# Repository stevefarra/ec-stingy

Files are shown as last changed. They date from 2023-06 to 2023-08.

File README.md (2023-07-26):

<p align="center">
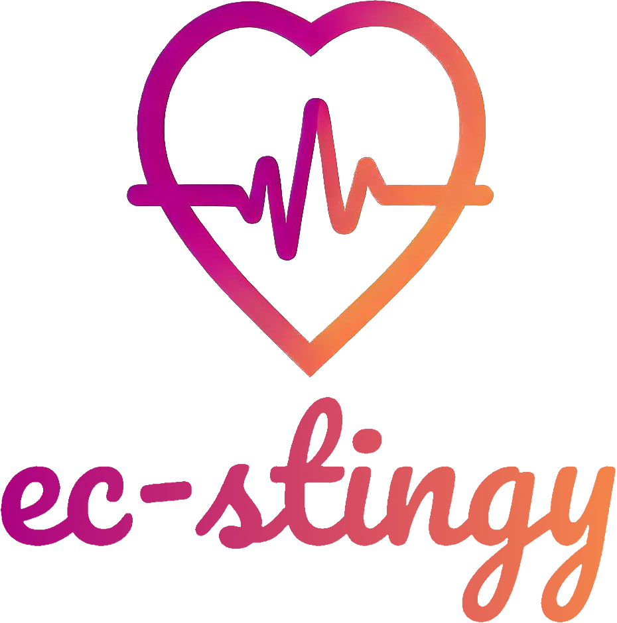
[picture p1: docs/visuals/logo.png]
Project logo
  
</p>

# ec-stingy
The EC(stin)G(y) provides an end-to-end design and implementation of a cost-effective, compact electrocardiogram. It connects to a computer via USB, monitoring a patient's cardiac signal and heart rate over time.

This project can serve as a template for any device measuring the heart's electrical activity and can be easily adapted to the user's needs. By open-sourcing the design files and code, the project aims to make medical hardware and technology more accessible and reduce the barrier to entry for prototyping.

## Directory Overview
Each folder corresponds to a specific stage of development or a component of the final product.

[`algorithm/`](algorithm/) - A simulation suite for prototyping digital signal filtering and peak detection.

[`firmware/`](firmware/) - Contains the program loaded into the MCU on-board the PCB.

[`spice/`](spice/) - Another simulation suite for prototyping the ECG analog front-end circuitry.

[`pcb/`](pcb/) - Schematic, footprint, and manufacturing files for the printed circuit board.

[`gui/`](gui/) - A desktop program to view the cardiac signal and heart rate readings over time.

[`docs/`](docs/) - Datasheets, README graphics, cited research papers, and other miscellanea.

## License

ec-stingy is licensed under the [MIT License](LICENSE). Unless otherwise stated, the repository owner authors all content, including source code, schematics, documentation, plots, animations, etc.

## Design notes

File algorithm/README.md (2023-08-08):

# Algorithm prototyping
## Directory overview
[`algorithm.m`](algorithm/algorithm.m) - An Octave script for design, implementation, and visualization of the signal conditioning, R-peak detection, and heart rate calculation program used by this project.

[`algorithm.c`](algorithm/algorithm.c) - A real-time C adaptation of the program contained in the Octave script, optimized for minimal time and memory complexity.

[`plot_output.m`](algorithm/plot_output.m) - An Octave script to plot the output waveforms produced by the C program, for debugging purposes.

[`scope.csv`](algorithm/scope.csv) - Several seconds of an ECG signal captured by a serial oscilloscope for testing purposes; see [`firmware/`](firmware/) for more details about the prototype used to capture this data.
## Design process
### Hum's the Word: Removing powerline interference
Before starting, we would like a signal that closely replicates what the ADC on our final PCB would read. Stock configuration on the AD8232 evaluation board is intended for measurements taken from the hands and has a passband of 7 to 24 Hz, which we will very likely modify for our final design. However, the algorithm should be resilient to changes in filtering and should therefore be valid for our purposes here.

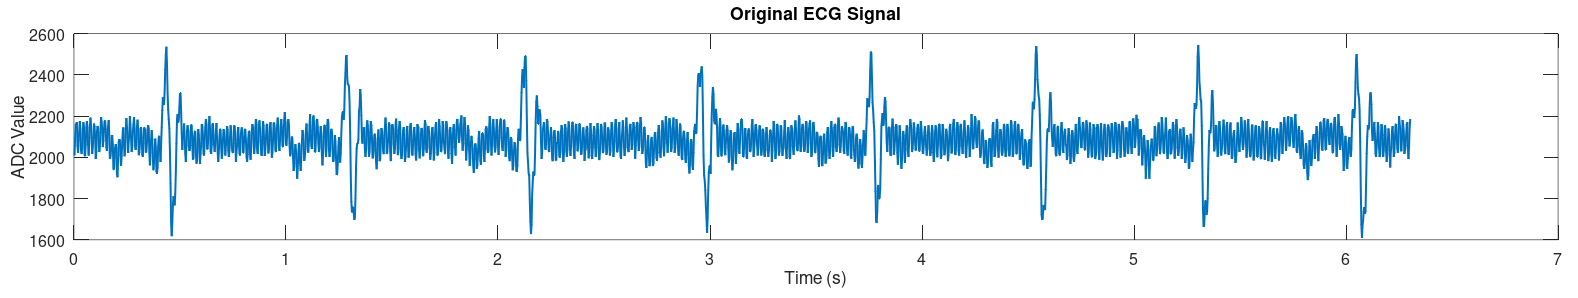
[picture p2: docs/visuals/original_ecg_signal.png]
Original ECG signal


The raw signal presents three immediate challenges:
1. Large DC offset
2. Mains noise prevalence
3. Noticeable waveform distortion (P and T waves are indiscernable)

We know the DC component dominates, so let's discard it before plotting the frequency spectrum up to the Nyquist frequency of 180 Hz:

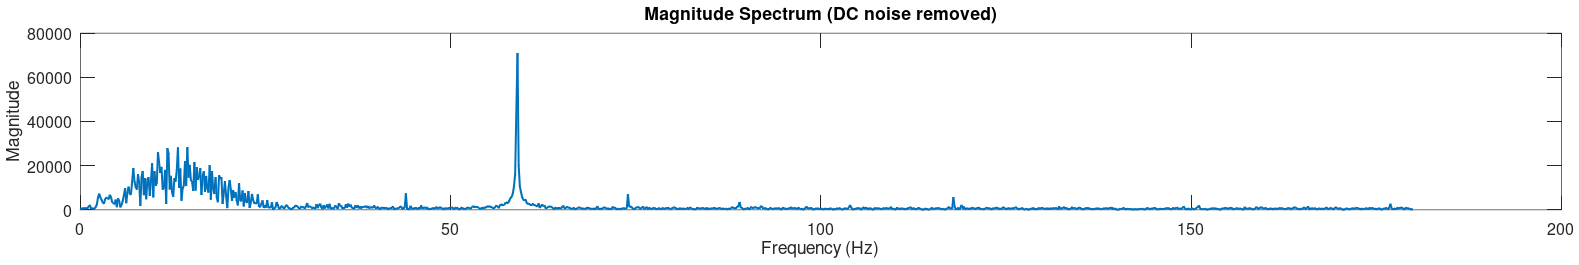
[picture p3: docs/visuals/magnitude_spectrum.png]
Magnitude spectrum


The narrow passband means that signal contents lay in the 0-30 Hz range with a dominant frequency at exactly 60 Hz, confirming our observation about the mains hum earlier. We want this design to work with electrode cables without any EMI shielding and we also want to retain the ability to use the signal for cardiac monitoring, so filtering will have to be done in the digital domain. A Notch filter allows us to strongly attenuate this particular frequency while introducing minimal distortion to the rest of the signal.

Using Octave's `pei_tseng_notch()` function means we only need to use a bit of trial-and-error to find the minimum bandwidth that effectively suppresses the 60 Hz noise, which visually occurs around 5 Hz, and yields a filter with an attentuation reaching nearly -30 dB:

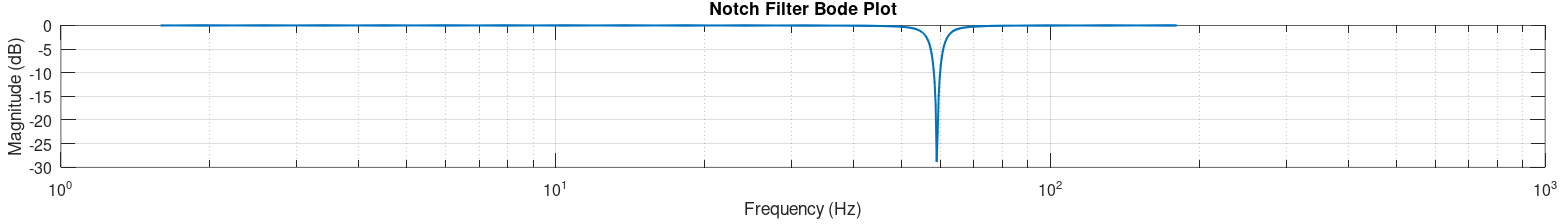
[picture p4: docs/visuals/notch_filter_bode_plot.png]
Notch filter bode plot


Here is the resultant signal, which now has something resembling a P-wave. The DC offset is still present but is addressed during R-peak detection, detailed below.

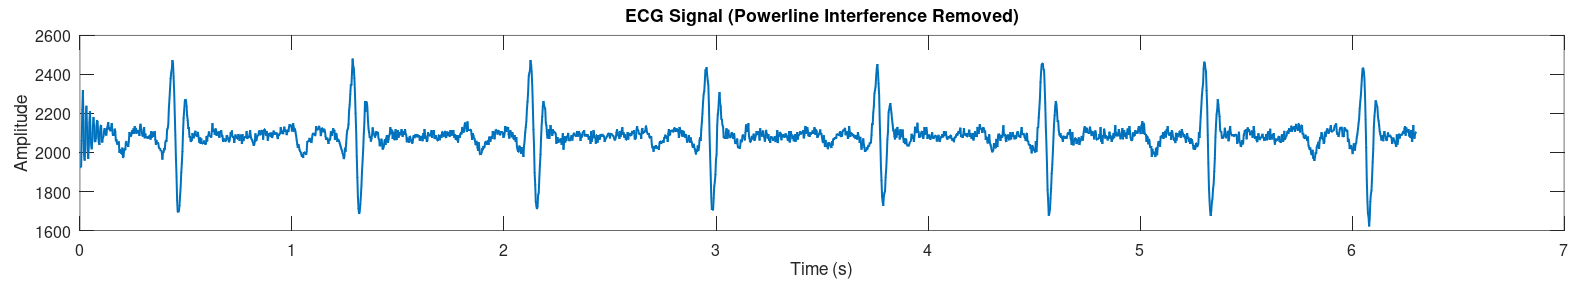
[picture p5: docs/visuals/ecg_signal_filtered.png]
Filtered ECG signal


### A Tribe Called QRS: Implementing heart rate detection
Every prominent R-peak detection algorithm has three distinct stages: signal conditioning, thresholding, and R-peak searching. This project uses an algorithm by Nguyen at al. that improves upon previous approaches by introducing a triangle template matching filter to reduce the resource complexity present in other algorithms used in embedded devices ([1](#references)). 

The signal conditioning filters depend on a set of parameters that depend on the sampling frequency $f_\text{s}$. The paper provides their recommendations for the canonical rate of $f_\text{s} = \text{360 Hz}$ as well as a procedure for determining some of them given $f_\text{s}$.

<div align="center">

| Parameter | Description | Value |
|---|---|---|
| $f_\text{s}$ | Sampling frequency | $\text{360 Hz}$ |
| $N$ | $h[i]$ window radius | $25$ |
| $s$ | $t[i]$ parameter | $7$ |
| $L$ | $l_1[i]$ window radius | $5$ |
| $M$ | $l_2[i]$ window radius | $150$ |
| $\beta$ | Threshold coefficient | $2.5$ |
| $\theta$ | Threshold offset | $\text{mean}(l_1[i])/4$ |

</div>

With the parameters set, we introduce some notation for a moving average filter centered around the current element (assume the signal is zero-padded):

$$\text{MA}(x[i],R):=\frac{1}{2R+1}\sum_{-R}^{R}x[i+R]$$
And the triangle template matching filter:
$$\text{TR}(x[i],R):=(x[i]-x[i-R])(x[i]-x[i+R])$$
With our notched ECG signal above denoted as $\text{ECG}[i]$, we begin cascading filters. The first is a high-pass filter:
$$\overline{\text{ECG}}[i] = \text{MA}(\text{ECG}[i],N)$$
$$\hat{h}[i] = \text{ECG}[i] - \overline{\text{ECG}}[i]$$
$$h[i] = |\hat{h}[i]|$$
With DC noise and negative values forgone, we have a signal suitable for peak detection:

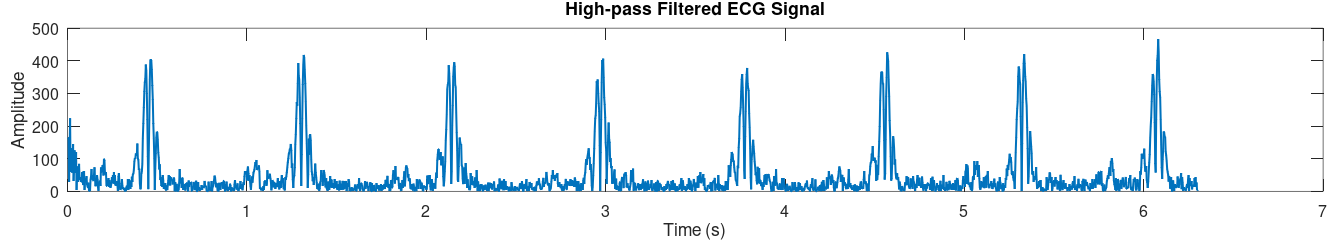
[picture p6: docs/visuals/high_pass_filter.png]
High pass filter


Next is the triangle filter, $t[i]=\text{TR}(h[i],s)$, which accentuates the QRS complex:

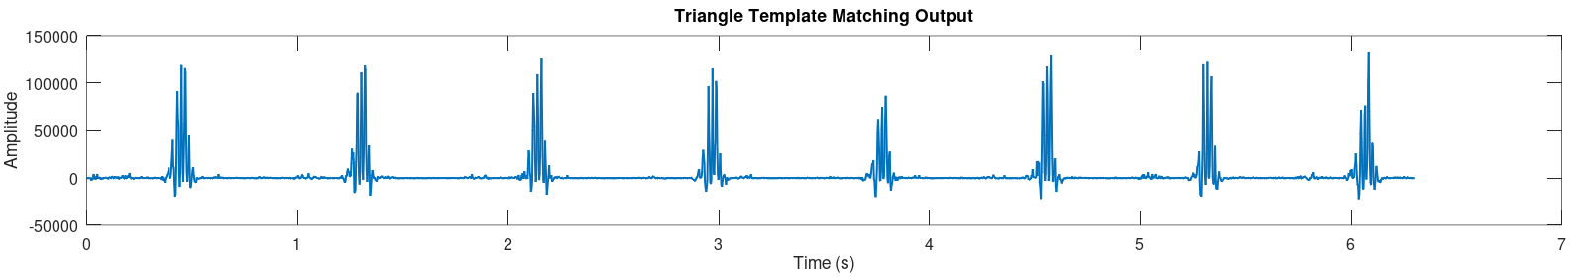
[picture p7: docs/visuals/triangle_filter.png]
Triangle


Finally, the thresholding filters:
$$l_1[i] = \text{MA}(t[i],L)$$
$$l_2[i] = \text{MA}(t[i],M)$$
$$\text{threshold}[i] = \beta l_2[i] + \theta$$

The first low pass filter, $l_1$, is used to "smoothen out" the output of the triangle filter while $l_2$ is used to set the threshold value. The result is

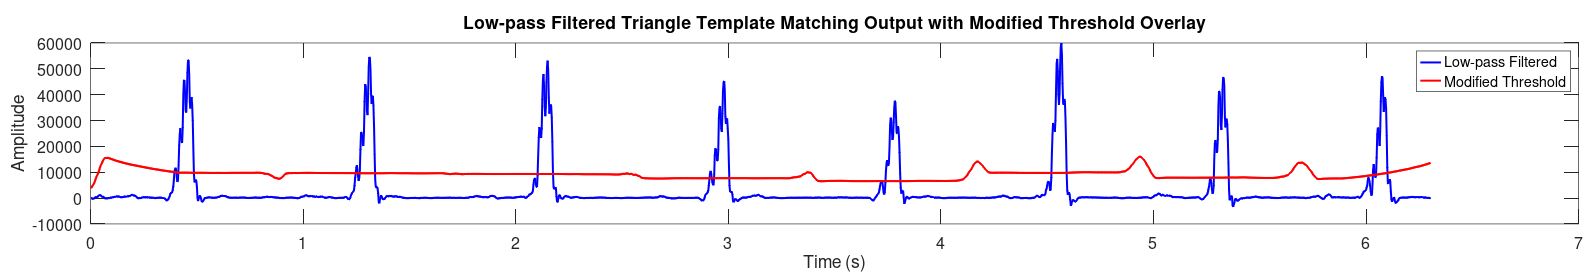
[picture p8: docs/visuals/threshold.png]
Threshold


Regions where $l_1$ (blue plot) is greater than the threshold value (red plot) are considered an AOI (area of interest) and maxima within each area are considered R-peaks. An error correction step must also be applied, however. Because the peaks produced by $l_1$ are not perfectly convex, AOIs that should be one contiguous region are sometimes detected as two separate regions. For an example of this, notice how the fourth QRS region in $l_1$ crosses the threshold, dips back down, and crosses over once again, resulting in false positives. To ameliorate this, the algorithm leverages the fact that the the theoretical maximum heart rate is 206 bpm, so when a detected R-R interval which exceeds this value the lower amplitude R-peak is discarded. With these rules applied, the detected R-peaks look like:

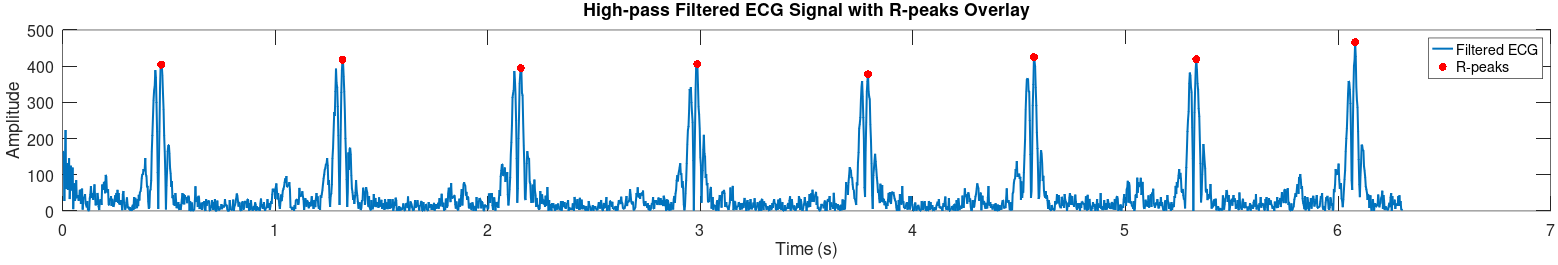
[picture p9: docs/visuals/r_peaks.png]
R-peaks


The heart rate readings, in units of bpm, are trivially calculated as $60/\text{RR}$, where $\text{RR}$ is the distance between successive R-peaks.

### Silence of the RAMs: Adaptations for a real-time environment

A naively implemented moving average filter poses a problem for real-time systems, which continuously compute filter outputs:
1. It requires division of very large numbers, or numerous (in our case, hundreds of) division operations to compute a single point.
2. It's noncausal, meaning we'll need to introduce signal buffers and keep track of how many samples have been read.

Let's begin with the recursive definition of the moving average filter:

$$\text{MA}(x[i],R):=\text{MA}(x[i-1],R)+\frac{1}{2R+1}\biggl(x[i+R]-x[i-(R+1)]\biggr)$$

This is a lot more efficient, but still requires the first $2R+1$ outputs to be computed before the outputs are valid, so we use an accumulator to incrementally compute the average before "turning on" the subsequent filter. Also note that the centering of the window is irrelevant, and only the number of samples read must be kept track of. This leads to the following pseudocode:

```
macro window(R)
    2 * R + 1
end macro

acc = 0
num_samples = 0

while true do
    acc = acc + newest_val / window(R)
    
    if num_samples > window(R) then
        acc = acc - oldest_val / window(R)
    end if

    num_samples = num_samples + 1
end while
```

In this case `oldest_val` is the sample which just outside of the current sampling window, which means that the buffer size for a signal that is moving average-filtered must be one greater than the window size, or $2R+2$.

For the signal being fed into the reverse template matching filter, $h[i]$, the domain varies from $i-R$ to $i+R$ so the input signal buffer size need only be equal to $2R + 1$. The computation is relatively simple so no optimizations are needed.

Our final consideration is the value of $\theta$ in the threshold computation. The paper this algorithm is based upon states that $\theta$ *could be one-fourth of the statistical mean of the output of the low-pass filter*, and they go on to use a pre-determined value calculated on their expansive database. Because we don't have this luxury, we leverage the fact that our second low-pass filter uses a large enough window size that the difference between its output and the true mean of the signal is negligible so we can set $\theta = l_2[i] / 4$ and compute it in real time.

## The Idea Graveyard
**More rigorous testing:** While the authors of the peak detection algorithm have thoroughly tested it on the MIT-BIH Arrhythmia Database and benchmarked it against several other popular algorithms, our proprietary real-time adaptation could benefit from additional validation. This could include unit testing helper functions and computing error in time differences (compared to ground truth data) between R-R peaks that are introduced by rounding and truncation in the C language.

**Use an FIR notch filter:** A significant advantage of our peak detection algorithm is its exclusive use of finite impulse response (FIR) filters for all necessary signal conditioning. This ensures stability, linear phase, and prevents potential positive feedback loops from quantization noise or electrode issues. Our additional Notch filter uses past output values and is therefore an IIR filter, but a [wise choice of zeroes](https://tttapa.github.io/Pages/Mathematics/Systems-and-Control-Theory/Digital-filters/FIR-Notch.html) for the transfer function might make an FIR filter with our desired characteristics possible.

**Employ a state machine:** The current real-time implementation relies on nested if-statements to manage delays between cascaded filters and execute the peak detection logic. A single state machine would increase code legibility and make debugging an easier task.

**Replace linear buffers with a deque:** Our current real-time implementation uses arrays as signal buffers, which are shifted every sampling period once filled. However, only 5 operations are needed to compute any filter in the R-peak detection algorithm:

  - `peek_front()`
  - `pop_front()`
  - `peek_rear()`
  - `pop_rear()`
  - `peak_middle()`
  
  A double-ended queue could be implemented to easily include these functions. Doing so would mean we wouldn't waste so many clock cycles shifting arrays. However, a deque requires storing the memory address of each node. Given that RAM size is a more restrictive factor than processing power in our case, we chose to use linear buffers. This keeps the stack size under 5 kB.

## References

[1]: T. Nguyen, X. Qin, A. Dinh, and F. Bui, "Low Resource Complexity R-peak Detection Based on Triangle Template Matching and Moving Average Filter," in *Sensors*, vol. 19, no. 18, article 3997, 2019. [Access Article](https://doi.org/10.3390/s19183997)

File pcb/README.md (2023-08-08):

# PCB Design

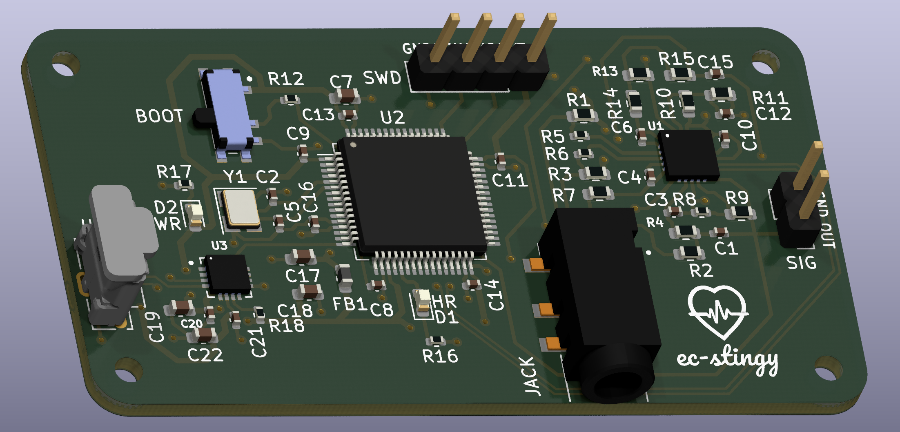
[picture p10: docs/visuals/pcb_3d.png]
3D PCB


## Directory overview
This directory includes several files with project metadata, but the key files are:

[`pcb.kicad_pro`](pcb.kicad_pro): KiCad 6 project file. Use this to properly load and open the schematic and layout files.

[`pcb.kicad_sch`](pcb.kicad_sch): The schematic file.

[`pcb.kicad_pcb`](pcb.kicad_pcb): The layout file.

[`libraries/`](libraries/): Contains symbols, footprints, and 3D models for components used in the project that are included in the KiCad library.

[`manufacturing/`](manufacturing/): Contains a bill of materials, a component placement file, and gerber files required to get the board produced.

## V for Via: Establishing a workflow
We heavily based the overall design and microcontroller layout on the [KiCad 6 STM32 tutorial](https://www.youtube.com/watch?v=aVUqaB0IMh4&pp=ygUNc3RtMzIga2ljYWQgNg%3D%3D), with several notable additions:

- The AD8232 and all of its associated circuitry (a near replica of the SPICE model in this project)
- The CP2102N USB-to-UART bridge controller, which acts as both a voltage regulator and PC interface in this design

We also added several peripherals to facilitate use and debugging:

- A micro-USB port, to power the board
- A 3.5 mm jack, to plug the electrode cable into
- A boot switch, to reset the microcontroller
- A serial wire debug pin header, to modify the firmware
- An ECG signal pin header, to inspect the analog signal
- LEDs to indicate a power connection and heartbeat readings, respectively

The schematic ends up falling roughly into 5 sections:

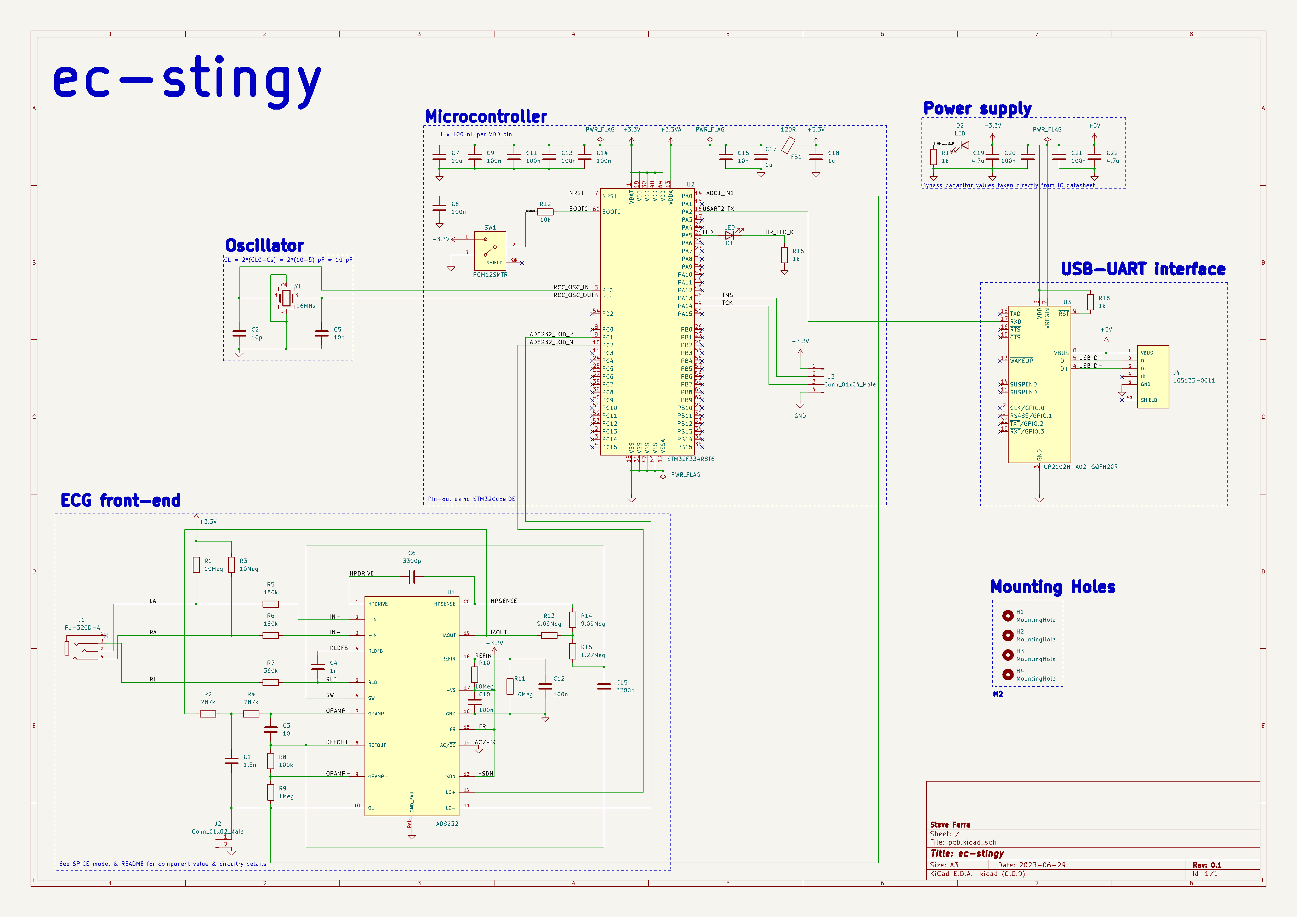
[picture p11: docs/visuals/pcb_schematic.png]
PCB Schematic


Before approaching the layout, we first consult PCB layout guidelines provided by the various ICs used. From the AD8232 datasheet:

> Keep all of the connections between high impedance nodes as short as  possible to avoid introducing additional noise and errors from  corrupting the signal. To maintain high CMRR over frequency, keep the input traces  symmetrical and length matched. Place safety and input bias  resistors in the same position relative to each input. In addition,  the use of a ground plane significantly improves the noise rejection of the system.

And from the STM32 datasheet:

> Each power-supply pair (VDD/VSS, VDDA/VSSA etc..) must be decoupled with filtering  ceramic capacitors as shown above. These capacitors must be placed as close as possible to or below the appropriate pins on the underside of the PCB, to ensure the good functionality of the device. The 10 nF capacitor must be ceramic (good quality) and it must be placed as close as possible to the chip.

With these principles in mind, a heavy draw of inspiration from the layout of the [SparkFun AD8232 breakout](https://www.sparkfun.com/products/12650), and a modest amount of trial-and-error, the resultant two-layer board layout came out like so:

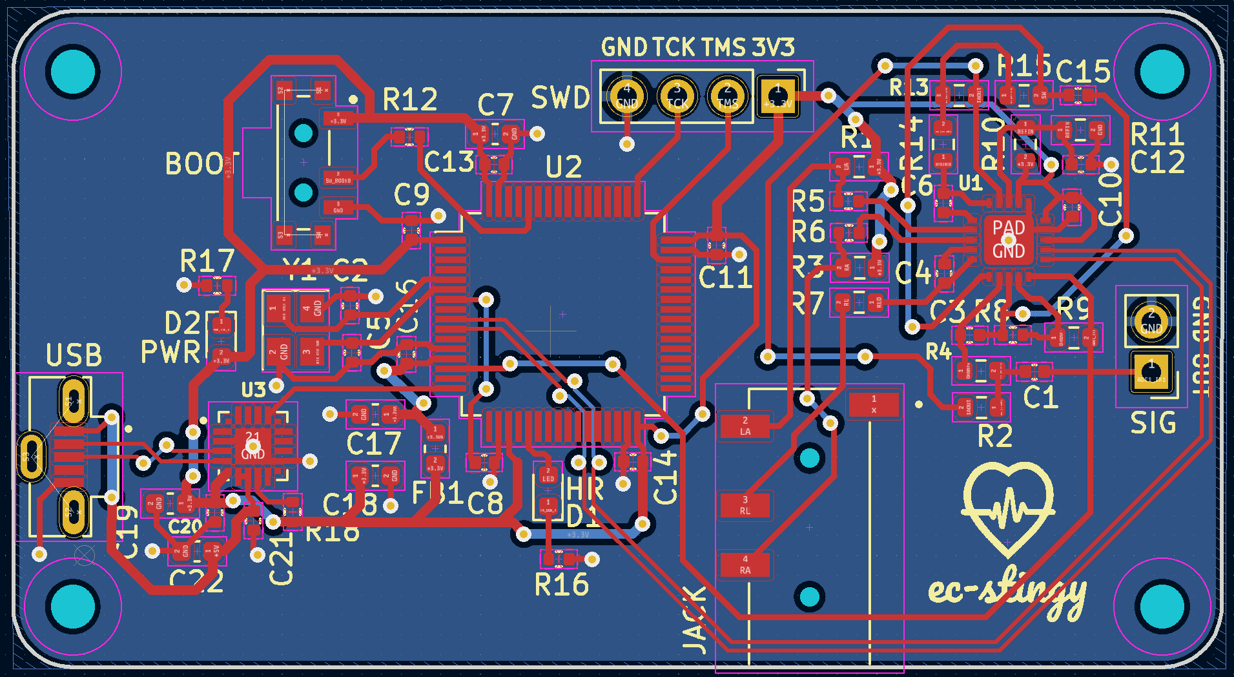
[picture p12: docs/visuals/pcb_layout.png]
PCB Layout


## How cost-effective is it, really?
Time and effort were put into ensuring that the components chosen were economical and readily available to reduce the manufacturing cost as much as possible. Below is a breakdown of the per-board manufacturing costs at the time of writing this, ordering from JLCPCB (minimum quantity of 5):

<div align="center">

| Category   | Cost (CAD)  |
|------------|-------------|
| Passives   | $0.50       |
| Connectors | $1.13       |
| ICs        | $6.86       |
| Assembly   | $3.07       |

</div>

Although it's difficult to directly compare this device to commercially-available products, the closest would be a Holter monitor like the [Prince 180B1 from Heal Force](http://www.healforce.com/en/html/products/portableecgmonitors/605.html) which currently retails at \$140 CAD. The total cost of our board comes to $11.56 CAD, which is roughly 9% of the market equivalent. Not bad!

## The cutting room floor
**Commission a board review:** Despite passing KiCad's electrical and design rule checks, a third-party formal review could validate the schematic and layout. This review would also ensure adherence to best practices on differential trace length matching, passive component sizing, and decoupling capacitor layout, helping to prevent potential costly or time-consuming errors before manufacturing.

**Add more safeguards:** This device is far from being fully IEC 60601-compliant, but replacing the PC power supply with an external battery, adding TVS diodes to sensitive traces for ESD protection, and using an optocoupler to provide electrical isolation between the patient and the ECG would all increase the device's overall safety.

**Compactify the layout:** The board size comes in at roughly 61 mm by 33 mm, but there is still quite a bit of unused space which could be used for more peripherals or done away with altogether by rearranging components.

**Design an enclosure:** A hard casing with cutouts for peripheral access and LED viewing could enhance this project. The board already has mounting holes for fastening. KiCad's [StepUp](https://www.kicad.org/external-tools/stepup/) tool allows the 3D model above to be easily imported into FreeCAD and would come in handy here.

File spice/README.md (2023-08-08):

# SPICE simulations
## Directory overview
[`ecgsyn.m`](spice/ecgsyn_m), [`derivsecgsyn.m`](spice/derivsecgsyn.m) - These are MATLAB scripts from [ECGSYN](https://physionet.org/content/ecgsyn/1.0.0/), a realistic ECG waveform generator. They are used in this project by [`gen_ecg.m`](gen_ecg.m).

[`gen_ecg.m`](spice/gen_ecg.m) - An Octave script for generating an ECG waveform suitable for transient analysis in LTspice.

[`AD8232.cir`](spice/AD8232.cir) - An LTspice model for the AD8232 chip, which is the analog front-end of choice for this project.

[`AD8232.asy`](spice/AD8232.asy) - An LTspice symbol for the AD8232.

[`ecg_front-end.asc`](spice/ecg_front-end.asc) - This LTspice schematic configures the AD8232 as used on the PCB, containing simulation commands for both frequency and transient analyses.

## Ohm is Where the Heart is: Widening the filter passband

This project employs the AD8232 to communicate with the MCU, providing a signal appropriate for the ADC. The datasheet for this IC provides several example configurations depending on the use case. We want to introduce minimal signal distortion at this stage and use as wide of a passband as possible for maximum versatility. The application circuit with the largest bandwidth is the cardiac monitor configuration, which employs a 0.5 Hz two-pole high-pass filter followed by a two-pole, 40 Hz low-pass filter.

This configuration is a good starting point for our own design but will be insufficient for diagnostic purposes. A 2012 paper points out that interpreting the ST segment of an ECG should involve a cut-off frequency of 0.05 Hz, as frequencies like 0.5 Hz can significantly distort this segment ([1](#references)).

Although there doesn't seem to be a definitive cut-off on the high end, most sources suggest clinical ECGs typically have a cut-off of 100 or 150 Hz. There may be good reason to extend even further; recent research suggests that detection of myocardial ischemia, a certain heart condition, is improved through high-frequency QRS analysis, which commonly occurs in the frequency range between 150 and 250 Hz as detailed in the work of Patel and Bourque ([2](#references)). This extends far beyond our Nyquist frequency of 180 Hz, however, so to avoid changing our sample rate and diverging from industry standards we'll aim for a high pass frequency cut-off of 150 Hz.

We start by simulating the provided cardiac monitor configuration and then modifying it as needed. To ensure our set-up is correct, we compare the bode plot provided in the datasheet with our simulated version and ensure the midband gain, roll-off, and cut-off frequencies are consistent with one another using the cursor tool:

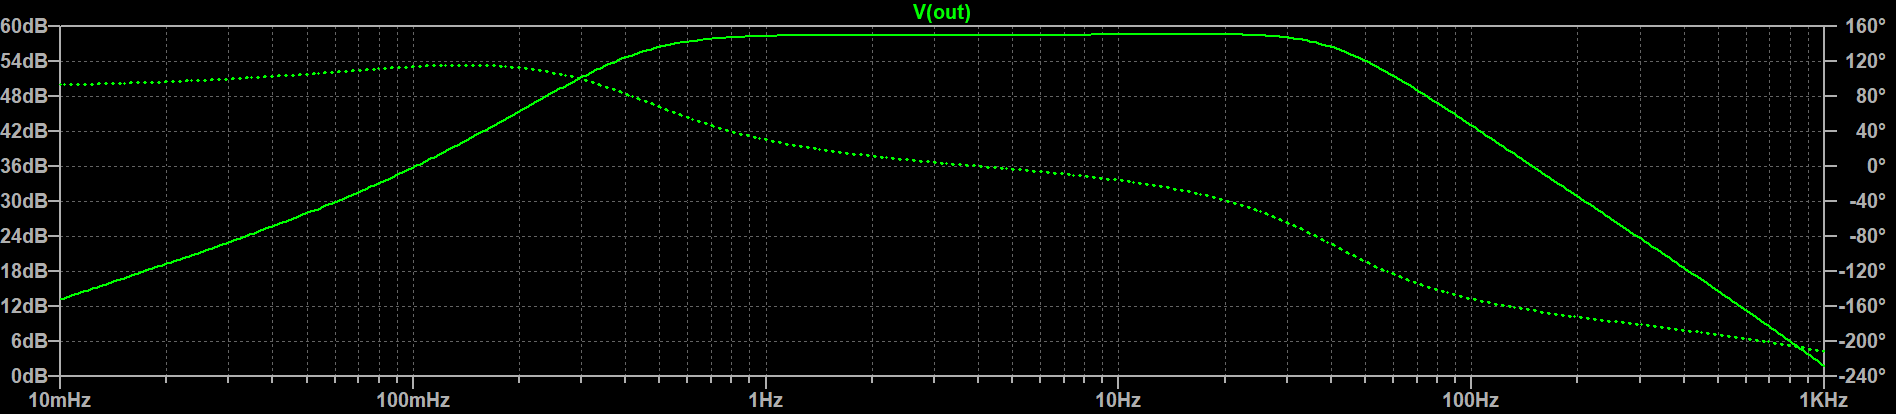
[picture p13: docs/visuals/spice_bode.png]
SPICE bode plot


We also perform a transient analysis with a simulated ECG signal sourced across the two leads:

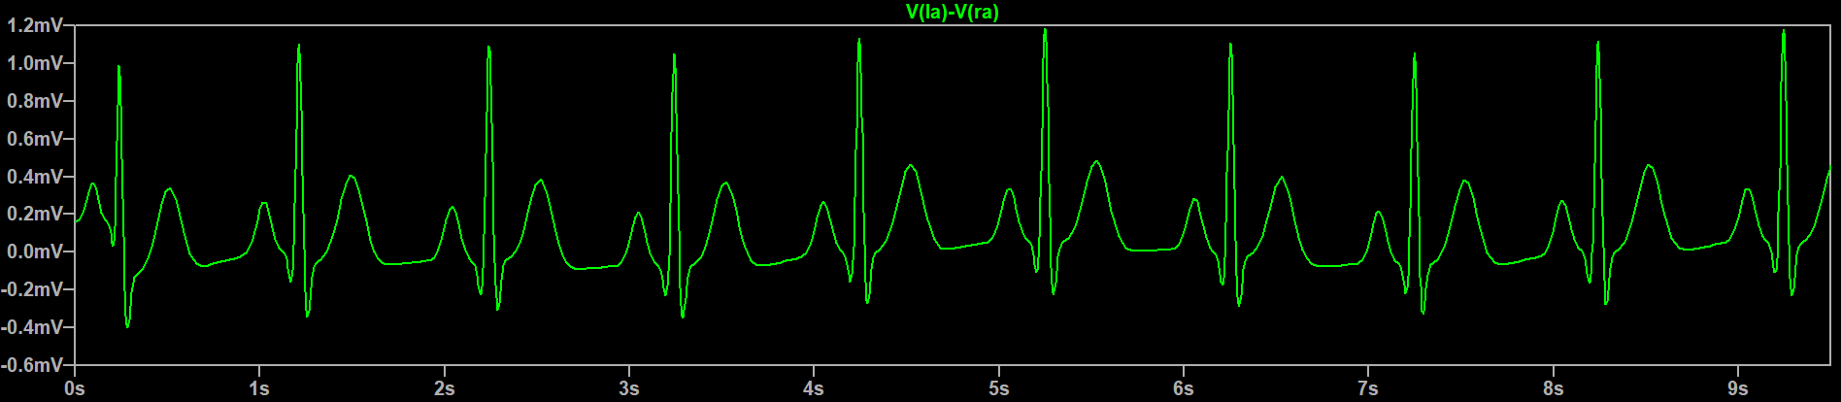
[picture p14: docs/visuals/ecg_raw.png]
Raw ECG


With a gain of 1100 and a passband of 0.5 to 40 Hz, our simulated output signal looks like:

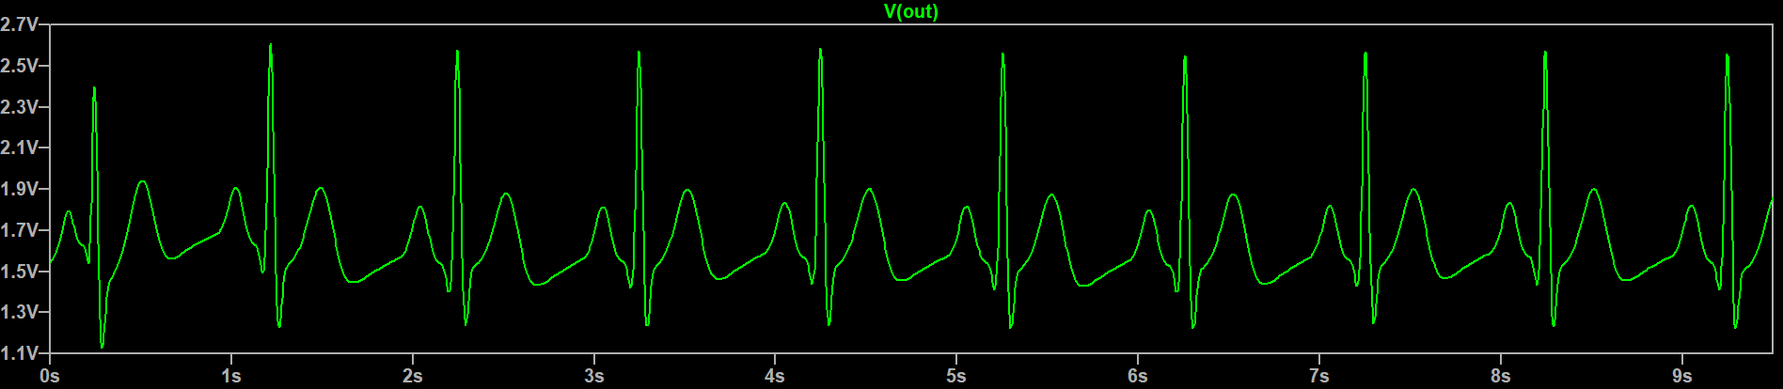
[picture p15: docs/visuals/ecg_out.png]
Output ECG


The filters have managed to remove the baseline wandering, added a DC offset, and amplified the signal considerably while preserving its general shape. Although the ST segment (and the distortion thereof) is hard to make out on this timescale, we can see the flatness of the TP segment is not present in the output.

### High-pass filter modification

Our design uses the high-pass filter topology from figure 56 of the datasheet. This includes an extra compensation resistor $R_\text{comp}$, enabling lower cut-off frequencies with reduced $R$ and $C$ values and finer control of the $Q$ factor. Deriving the transfer function from first principles is no trivial task because of the internal transconductance amplifiers and instrumentation amplifier in this stage. Luckily, the datasheet provides us with the cut-off frequency:
$$f_\text{c}=\frac{10}{2\pi \sqrt{R_1 C_1 R_2 C_2}}$$ And a recommended starting point for component value selection:
$$R_1 = R_2 \geq 100\text{ k}\Omega$$ $$C_1 = C_2$$ $$R_\text{comp} = 0.14R_1$$ with the caveat that the above selection of $R_\text{comp}$ optimizes for a maximally flat passband and choosing a value too low can result in an unstable circuit. Our starting configuration of $R_1 = R_2 = 10\text{ M}\Omega$ and $C_1 = C_2 = 0.33 \text{ }\mu\text{F}$ results in a cut-off frequency of about 0.48 Hz. To get to our desired value we only need to lower our cut-off frequency by an order of magnitude. Because our resistors are already quite large and changing their values substantially could lead to higher-order effects, we'll instead increase the size of both capacitors by a factor of 10 to 3300 pF. In simulation this places the cut-off frequency at about 45 mHz, so this time we tweak the resistor values. As mentioned by Bravo-Zanoguera et al., the IEC 60601 standard requires 1% component tolerances for medical devices ([3](#references)), so we round down to a resistor value from the E96 series and find that 9.09 MΩ resistors places the cut-off frequency at about 49 mHz. We also adjust the compensation resistor according to the recommendation above and modify its value to 1.27 MΩ. With these modifications, we re-run the transient analysis:

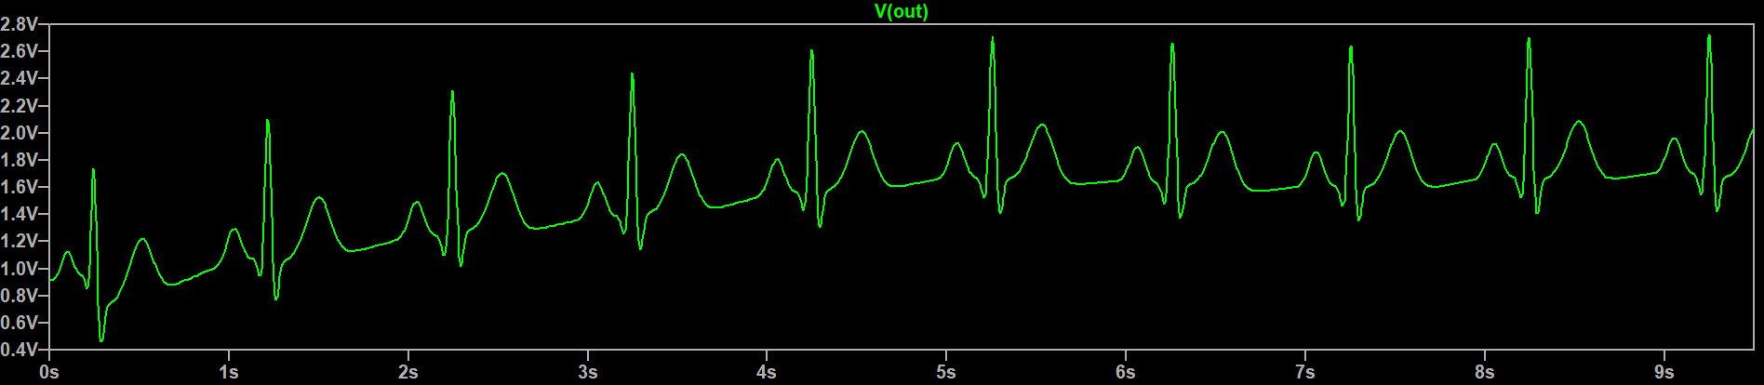
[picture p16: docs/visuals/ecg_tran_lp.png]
ECG Low pass transient anaylsis


The flatness of the TP segment is preserved, but now the signal takes several seconds to settle! As [this MEDTEQ article](https://www.medteq.net/article/2017/4/1/ecg-filters) explains, lowering the cut-off frequency raises the time constant. This is why the AD8232 includes a fast restore circuit, which briefly connects the filter to internal resistors that shift the poles to a higher frequency and drain $C_1$ and $C_2$ more quickly. It's unclear why the signal takes so long to settle despite the fact that fast-restore is enabled in simulation; the capacitors may simply need to be smaller for the effect to be more apparent. In any case, our digital high pass filter has an extremely fast settling time that takes care of this, so we proceed to modifying the low-pass filter.

### Low-pass filter modification

Our low-pass filter uses the Sallen-Key filter topology from figure 60 described by

$$f_\text{c}=\frac{1}{2\pi \sqrt{R_1 C_1 R_2 C_2}}$$

$$A_v=1+\frac{R3}{R4}$$

$$Q=\frac{\sqrt{R_1 C_1 R_2 C_2}}{R_1 C_2 + R_2 C_2 + R_1 C_1(1-A_v)}$$

At our current gain of $A_v = 11$, $C_2$ must remain several times larger than $C_1$ to maintain stability. Because the constraints on $R_1$ and $R_2$ are less delicate, we start by modifying the resistances. To find a starting point, we set $R_1=R_2$, $f_c=150\text{ Hz}$, and keep the capacitances the same, yielding $R_1=R_2 \approx 274\text{ k}\Omega$. In simulation this sets our cut-off to about 158 Hz, so we round both resistances up to the E96 value of 287 kΩ which corresponds to 151 Hz. With these component values, our $Q$ is also set at roughly 0.77, close to the recommended value of 0.7 for maximum passband flatness and sharp cut off. Here is the bode plot of our finalized design:

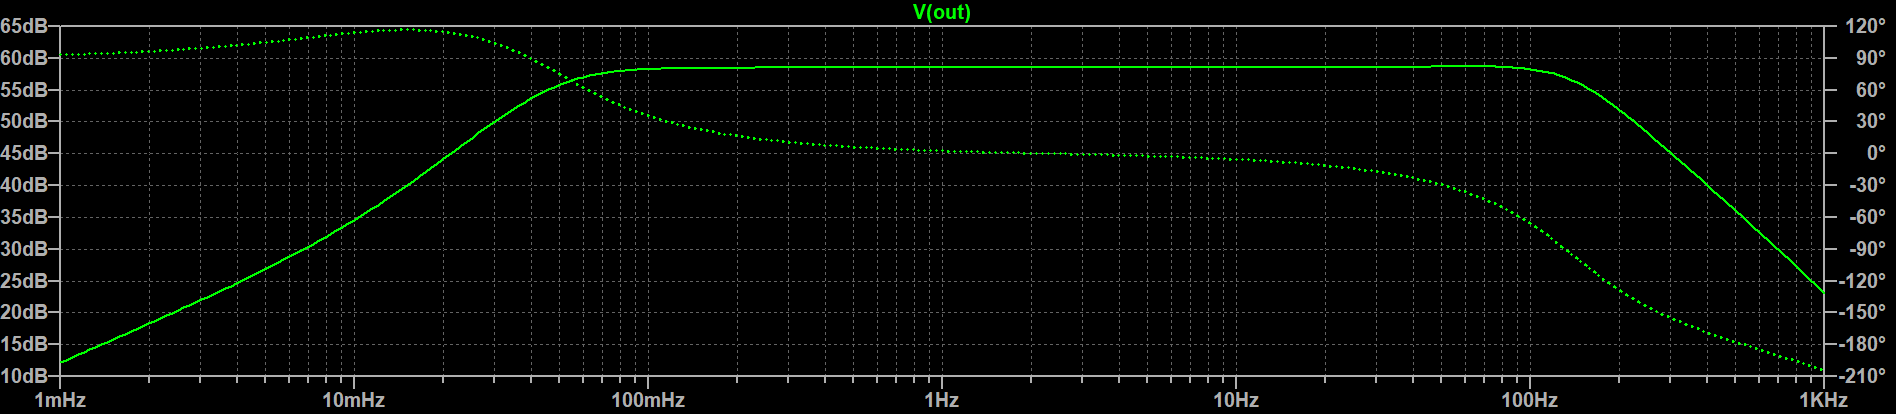
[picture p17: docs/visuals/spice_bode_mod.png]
ECG Bode plot final


## Idea Graveyard
**Build an analog front-end from scratch**: The idea of building the required circuitry using discrete ICs was considered, but the bill of materials just for core functionality—an in-amp, op-amps, and switches—quickly exceeded the current price for an AD8232, not to mention the jump in complexity. A high-performance instrumentation amplifier with a high CMRR (common-mode rejection ratio) and low VOS (input offset voltage) already cranks up the price. Barring future supply chain issues, this approach was quickly deemed unnecessary.

**Optimize the bill of materials:** While we chose filtering circuit components solely for performance, we could decrease manufacturing costs at scale by reducing the number of different parts and identifying where tolerances can be more relaxed.

## References

[1]: F. Buendía-Fuentes et al., "High-Bandpass Filters in Electrocardiography: Source of Error in the Interpretation of the ST Segment," in *ISRN Cardiology*, vol. 2012, article 706217, June 21, 2012. [Access Article](https://doi.org/10.5402/2012/706217)

[2]: T. R. Patel and J. Bourque, "High Frequency QRS analysis to supplement ST-Analysis for Myocardial Ischemia: multi-center prospective cohort," in *European Heart Journal - Cardiovascular Imaging*, vol. 22, no. Supplement_3, June 2021, jeab111.052. [Access Article](https://doi.org/10.1093/ehjci/jeab111.052)

[3]: M. Bravo-Zanoguera, D. Cuevas-González, M. A. Reyna, J. P. García-Vázquez and R. L. Avitia, "Fabricating a Portable ECG Device Using AD823X Analog Front-End Microchips and Open-Source Development Validation," in *Sensors*, vol. 20, no. 20, pp. 5962, October 21, 2020. [Access Article](https://doi.org/10.3390/s20205962)

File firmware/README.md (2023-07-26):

# Firmware
This directory houses an STM32CubeIDE project. It targets the STM32F334R8 board and runs a slightly modified version of [`algorithm/algorithm.c`](../algorithm/algorithm.c). You can immediately compile, flash, and run it with the IDE once the board is connected.
## Directory overview
[`Core/`](Core/): Contains source, header, and startup files for this STM32 project. All user-written code and documentation in this project is contained within [`Core/Src/main.c`](Core/Src/main.c).

[`Drivers/`](Drivers/): Contains device-specific drivers and hardware abstraction layer (HAL) files.

[`.mxproject`](.mxproject), [`firmware.ioc`](firmware.ioc): Used by STM32CubeMX to specify configuration information for this project (pin assignments, clock settings, peripheral configurations, etc.).

## The Right Chip for Your Salsa: Choosing a microcontroller

The STM32 family of microcontrollers was chosen for this project due to its comprehensive suite of development tools, extensive documentation, and vast range of devices, giving it a significant advantage over its competitors. The must-haves for this project are

- Two timers; one that triggers every sample period and another to flash an LED upon QRS detection
- An ADC with at least 12-bit resolution to capture the AD8232 output signal
- A dedicated FPU (floating point unit) for real-time signal processing
- A communication protocol to interface with a serial port, for debugging purposes and the GUI (this project uses USART)
- ~5 kB of RAM, largely used by signal buffers

The STM32F334R8 satisfies all of these requirements, is well-priced, and also had an in-stock development board that was ready to order.

## Minimalist Marvel: Assembling a barebones prototype for firmware testing

To develop and test the firmware on a real-time sampled signal, from electrode pads to the serial port, we used several development and breakout boards:

<div align="center">

| Part Number | Description |
|---|---|
| [AD8232-EVALZ](https://www.analog.com/en/design-center/evaluation-hardware-and-software/evaluation-boards-kits/eval-ad8232.html) | AD8232 evaluation board |
| [NUCLEO-F334R8](https://www.st.com/en/evaluation-tools/nucleo-f334r8.html) | STM32 Nucleo-64 development board |
| [BOB-11570](https://www.sparkfun.com/products/11570) | SparkFun TRRS 3.5mm jack breakout |
| [LD1117-3.3 TO-220](https://www.st.com/resource/en/datasheet/ld1117.pdf) | 3.3 V linear voltage regulator |
| [CAB-12970](https://www.sparkfun.com/products/12970) | SparkFun 3.5 mm jack to 3-electrode cable |
| [3M 2560](https://www.3m.com/3M/en_US/medical-us/red-dot-ecg-electrodes/) | 3M Red Dot monitoring electrode pads |

</div>

These parts can be connected using only jumper wires and a breadboard in the following manner:

<div align="center">

Prototype setup

</div>

Not included in this diagram is the electrode cable attached to the 3.5 mm jack breakout board, and a simple 9V battery snap connector attached to a Duracell CopperTop which powers the regulator. The Nucleo development board connects to a PC using a micro-USB cable. 

## The idea graveyard

**More safety guardrails**: An important notice is included in the datasheet for the AD8232 evaluation board:

> For safety reasons, Analog Devices, Inc., recommends evaluating the device with an electrocardiogram (ECG) signal source  instead of a live subject. Although the LA, RA, and RL electrode  terminals are equipped with current-limiting resistors (R3, R4, and R5), these resistors are not a comprehensive patient protection system. The resistors may not protect against supply line transients or leakage currents coming through power and acquisition systems. The user is fully responsible for understanding and applying all the safety guidelines and regulations that apply to medical equipment.

The author of this repository felt daring enough to use the aforementioned current-limiting resistors and a battery power supply as his insurance against any potentially dangerous occurences, but an arbitrary waveform generator could be used in place of a live subject, although it does not allow for use of the right leg drive electrode or the leads-out detection functionality of the AD8232.

**Optimize the choice of MCU**: The STM32F334R8 microcontroller, being more powerful than this project requires, leaves many of its peripherals and pins unused. Reducing manufacturing cost might involve a more optimized choice of MCU.

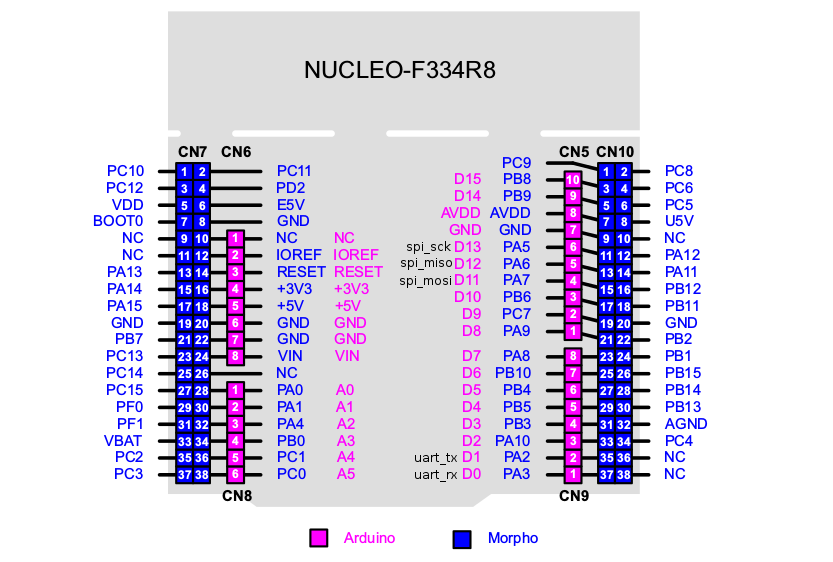
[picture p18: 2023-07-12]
docs/misc/nucleo-f334_pinout.png

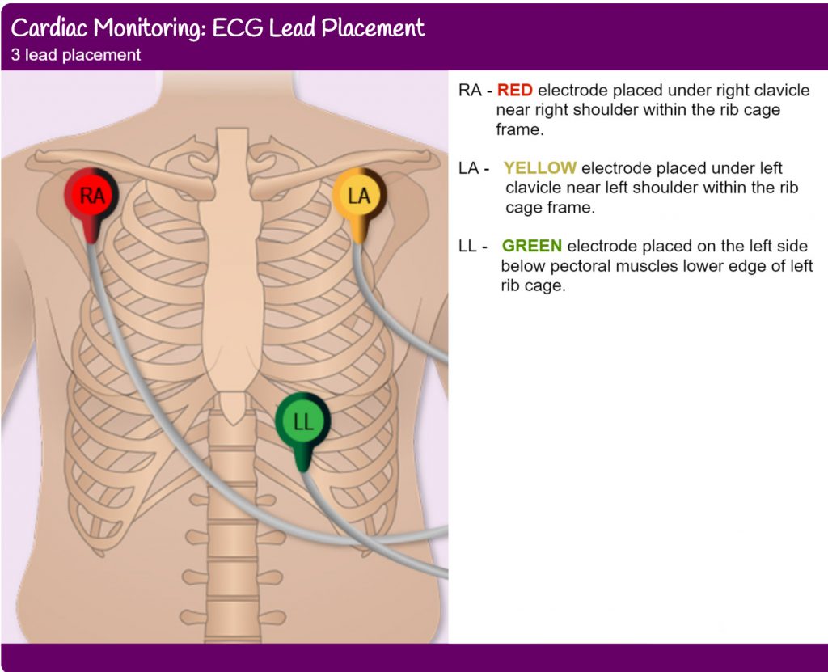
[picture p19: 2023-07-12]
docs/misc/lead_placement.jpg

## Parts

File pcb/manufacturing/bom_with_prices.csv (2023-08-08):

Source: |  |  |  | D:\Repositories\ec-stingy\pcb\pcb.kicad_sch
Date: |  |  |  | 2023-07-19 12:03:35 PM
Tool: |  |  |  | Eeschema (6.0.9)
Generator: |  |  |  | D:\Program Files\KiCad\6.0\bin\scripting\plugins/bom_csv_grouped_by_value_with_fp.py
Component Count: |  |  |  | 56
Ref | Footprint | Value | Price | Qnty | Total price | Cmp name | Description | Vendor
C1, | Capacitor_SMD:C_0402_1005Metric | 1.5n | 0.01 | 1 | 0.01 | C | Unpolarized capacitor
C2, C5, | Capacitor_SMD:C_0402_1005Metric | 10p | 0.0055 | 2 | 0.011 | C | Unpolarized capacitor
C3, C16, | Capacitor_SMD:C_0402_1005Metric | 10n | 0.0014 | 2 | 0.0028 | C | Unpolarized capacitor
C4, | Capacitor_SMD:C_0402_1005Metric | 1n | 0.0092 | 1 | 0.0092 | C | Unpolarized capacitor
C6, C15, | Capacitor_SMD:C_0402_1005Metric | 3300p | 0.0157 | 2 | 0.0314 | C | Unpolarized capacitor
C7, | Capacitor_SMD:C_0603_1608Metric | 10u | 0.0121 | 1 | 0.0121 | C | Unpolarized capacitor
C8, C9, C10, C11, C12, C13, C14, C20, C21, | Capacitor_SMD:C_0402_1005Metric | 100n | 0.0065 | 9 | 0.0585 | C | Unpolarized capacitor
C17, C18, | Capacitor_SMD:C_0603_1608Metric | 1u | 0.0108 | 2 | 0.0216 | C | Unpolarized capacitor
C19, C22, | Capacitor_SMD:C_0603_1608Metric | 4.7u | 0.0216 | 2 | 0.0432 | C | Unpolarized capacitor
D1, D2, | LED_SMD:LED_0603_1608Metric | LED | 0.0228 | 2 | 0.0456 | LED | Light emitting diode
FB1, | Inductor_SMD:L_0603_1608Metric | 120R | 0.0081 | 1 | 0.0081 | FerriteBead | Ferrite bead
R1, R3, R10, R11, | Resistor_SMD:R_0603_1608Metric | 10Meg | 0.0011 | 4 | 0.0044 | R | Resistor
R2, R4, | Resistor_SMD:R_0603_1608Metric | 287k | 0.0008 | 2 | 0.0016 | R | Resistor
R5, R6, | Resistor_SMD:R_0402_1005Metric | 180k | 0.0005 | 2 | 0.001 | R | Resistor
R7, | Resistor_SMD:R_0603_1608Metric | 360k | 0.0009 | 1 | 0.0009 | R | Resistor
R8, | Resistor_SMD:R_0402_1005Metric | 100k | 0.0014 | 1 | 0.0014 | R | Resistor
R9, | Resistor_SMD:R_0603_1608Metric | 1Meg | 0.0009 | 1 | 0.0009 | R | Resistor
R12, | Resistor_SMD:R_0402_1005Metric | 10k | 0.0017 | 1 | 0.0017 | R | Resistor
R13, R14, | Resistor_SMD:R_0603_1608Metric | 9.09Meg | 0.0024 | 2 | 0.0048 | R | Resistor
R15, | Resistor_SMD:R_0603_1608Metric | 1.27Meg | 0.0012 | 1 | 0.0012 | R | Resistor
R16, R17, R18, | Resistor_SMD:R_0402_1005Metric | 1k | 0.0021 | 3 | 0.0063 | R | Resistor
Y1, | Crystal:Crystal_SMD_3225-4Pin_3.2x2.5mm | 16MHz | 0.2227 | 1 | 0.2227 | Crystal_GND24 | Four pin crystal, GND on pins 2 and 4
J2, | Connector_PinHeader_2.54mm:PinHeader_1x02_P2.54mm_Vertical | Conn_01x02_Male | 0.0229 | 1 | 0.0229 | Conn_01x02_Male | Generic connector, single row, 01x02
J3, | Connector_PinHeader_2.54mm:PinHeader_1x04_P2.54mm_Vertical | Conn_01x04_Male | 0.0194 | 1 | 0.0194 | Conn_01x04_Male | Generic connector, single row, 01x04
J1, | PJ-320D-A:HRO_PJ-320D-A | PJ-320D-A | 0.0396 | 1 | 0.0396 | PJ-320D-A
J4, | 105133-0011:MOLEX_105133-0011 | 105133-0011 | 0.3889 | 1 | 0.3889 | 105133-0011
SW1, | PCM12SMTR:SW_PCM12SMTR | PCM12SMTR | 0.6625 | 1 | 0.6625 | PCM12SMTR
U1, | AD8232:LFCSP_20 | AD8232 | 1.6312 | 1 | 1.6312 | AD8232
U2, | Package_QFP:LQFP-64_10x10mm_P0.5mm | STM32F334R8T6 | 3.1411 | 1 | 3.1411 | STM32F334R8Tx | ARM Cortex-M4 MCU, 64KB flash, 12KB RAM, 72MHz, 2-3.6V, 51 GPIO, LQFP-64
U3, | CP2102N-A02-GQFN20R:SILABS_CP2102N-A02-GQFN20R | CP2102N-A02-GQFN20R | 2.0896 | 1 | 2.0896 | CP2102N-Axx-xQFN20 | USB to UART master bridge, QFN-20

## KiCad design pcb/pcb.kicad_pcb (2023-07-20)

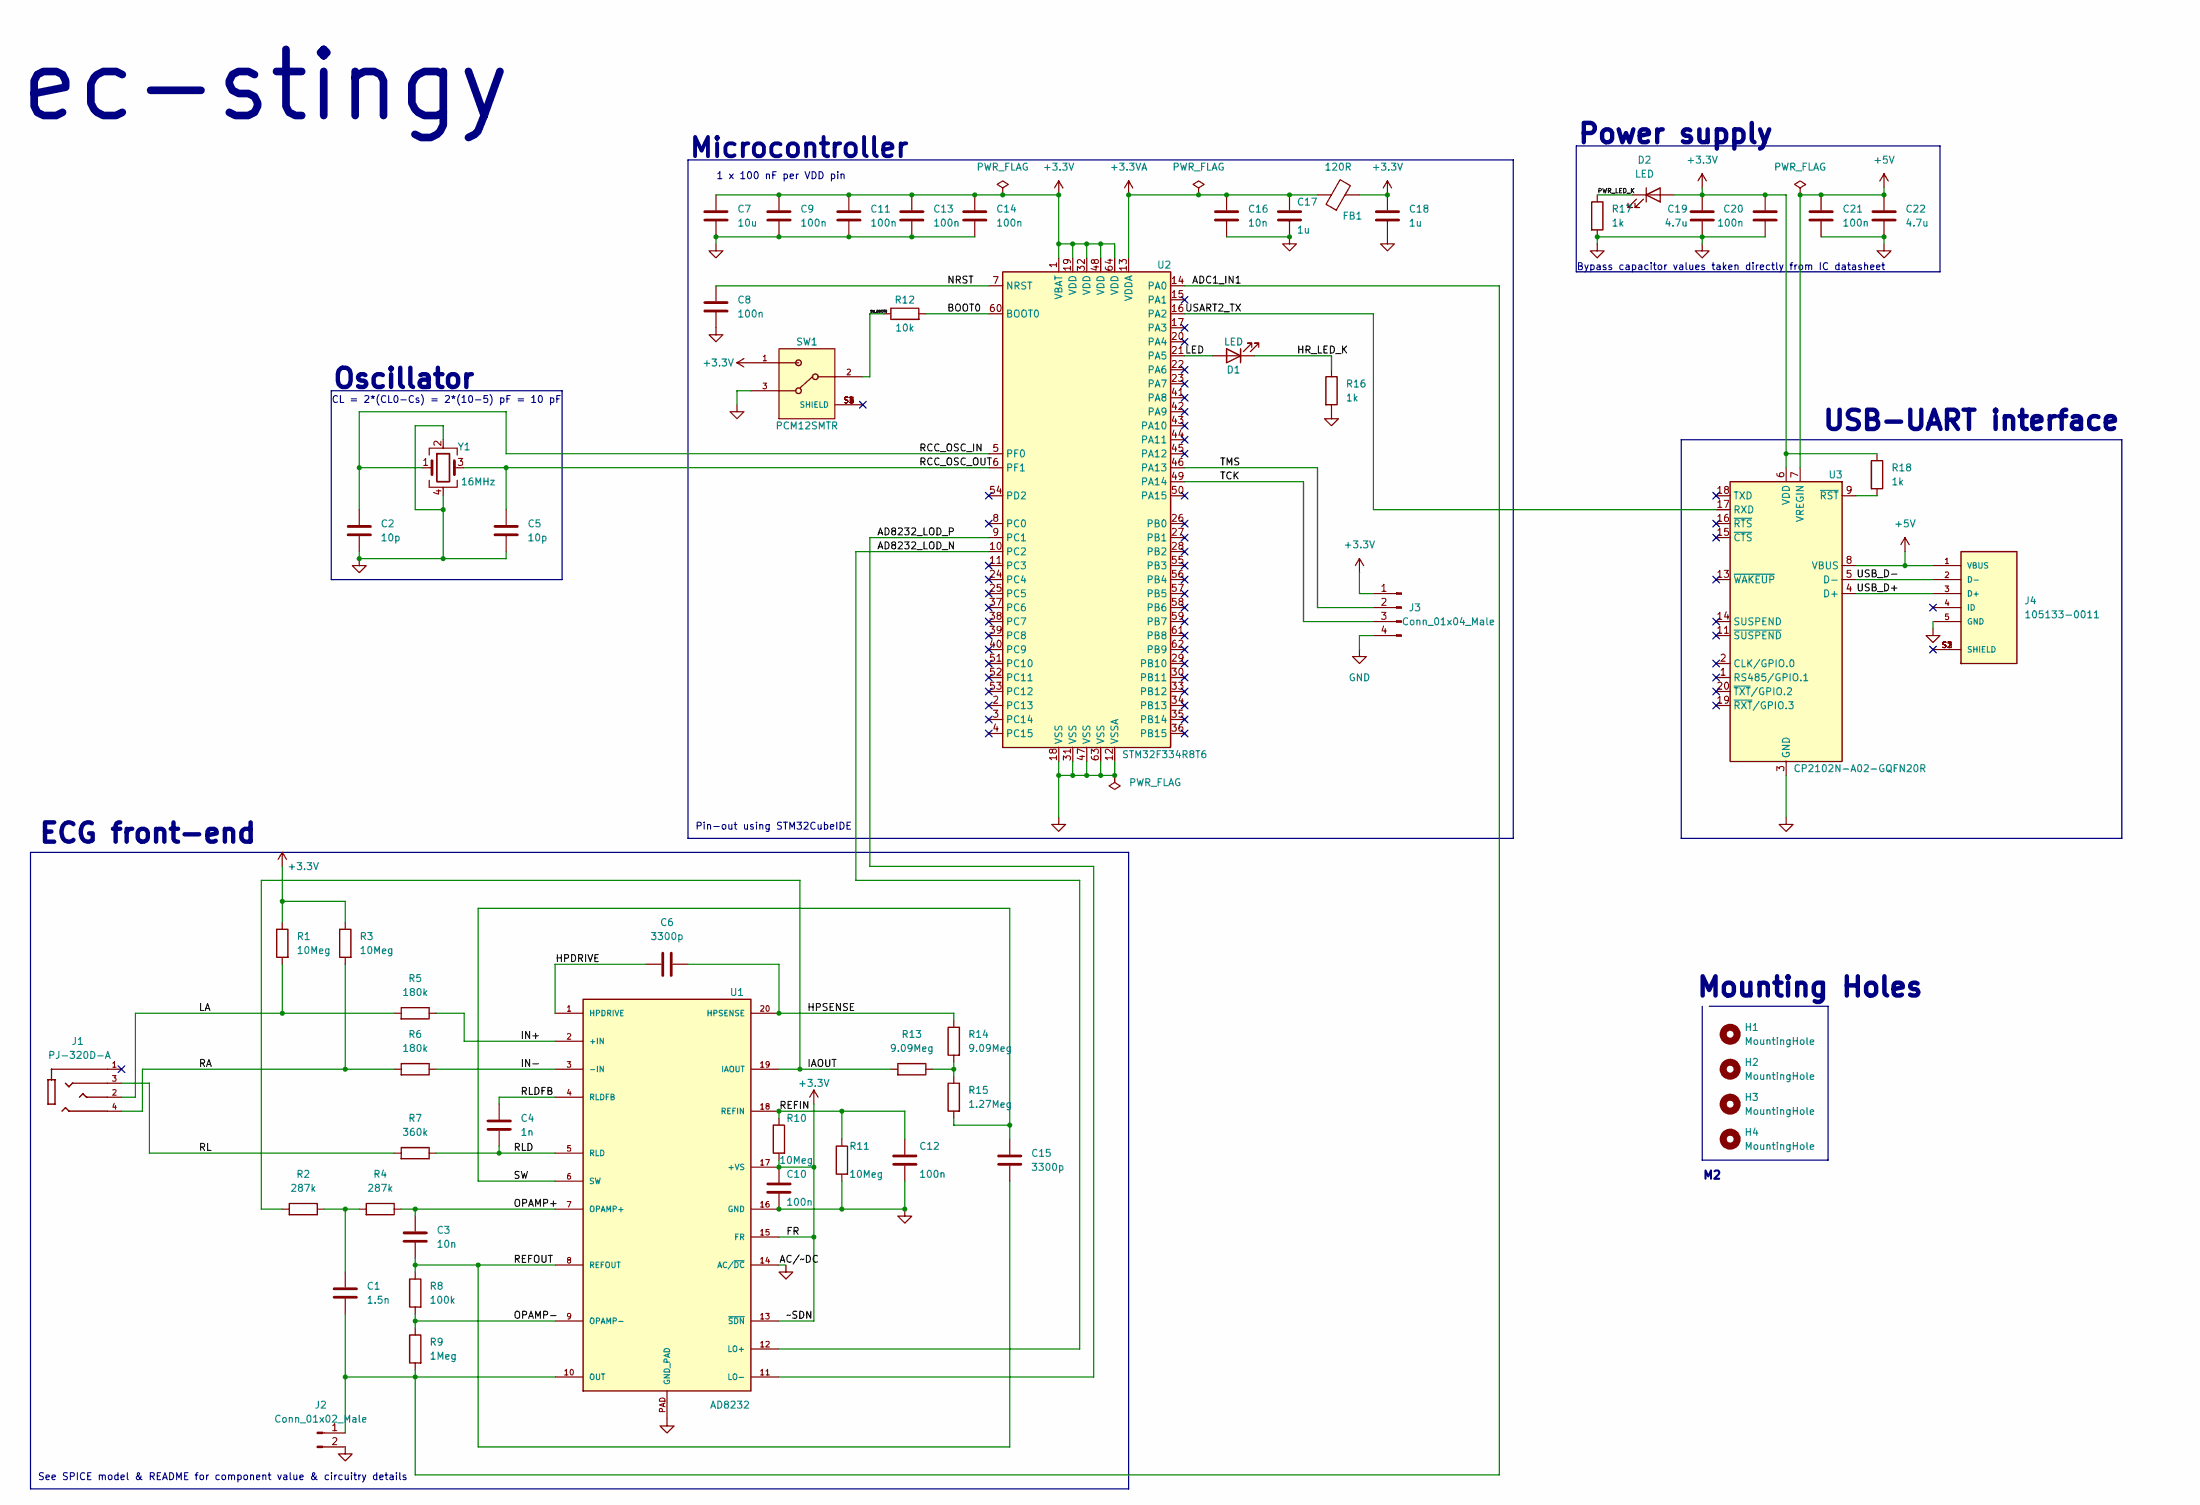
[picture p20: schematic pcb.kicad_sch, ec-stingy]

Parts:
C1: 1.5n; C_0402_1005Metric
C2, C5: 10p; C_0402_1005Metric
C3, C16: 10n; C_0402_1005Metric
C4: 1n; C_0402_1005Metric
C6, C15: 3300p; C_0402_1005Metric
C7: 10u; C_0603_1608Metric
C8, C9, C10, C11, C12, C13, C14, C20, C21: 100n; C_0402_1005Metric
C17, C18: 1u; C_0603_1608Metric
C19, C22: 4.7u; C_0603_1608Metric
D1, D2: LED; LED_0603_1608Metric
FB1: 120R; L_0603_1608Metric
H1, H2, H3, H4: MountingHole; MountingHole_2.2mm_M2
J1: PJ-320D-A; HRO_PJ-320D-A; PARTREV B
J2: Conn_01x02_Male; PinHeader_1x02_P2.54mm_Vertical
J3: Conn_01x04_Male; PinHeader_1x04_P2.54mm_Vertical
J4: 105133-0011; MOLEX_105133-0011; PARTREV C
R1, R3, R10, R11: 10Meg; R_0603_1608Metric
R2, R4: 287k; R_0603_1608Metric
R5, R6: 180k; R_0402_1005Metric
R7: 360k; R_0603_1608Metric
R8: 100k; R_0402_1005Metric
R9: 1Meg; R_0603_1608Metric
R12: 10k; R_0402_1005Metric
R13, R14: 9.09Meg; R_0603_1608Metric
R15: 1.27Meg; R_0603_1608Metric
R16, R17, R18: 1k; R_0402_1005Metric
SW1: PCM12SMTR; SW_PCM12SMTR
U1: AD8232; LFCSP_20
U2: STM32F334R8T6; LQFP-64_10x10mm_P0.5mm
U3: CP2102N-A02-GQFN20R; SILABS_CP2102N-A02-GQFN20R
Y1: 16MHz; Crystal_SMD_3225-4Pin_3.2x2.5mm

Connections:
+3.3V: C7.1, C9.1, C10.1, C11.1, C13.1, C14.1, C18.1, C19.1, C20.1, D2.2 (A), FB1.2, J3.1, R1.1, R3.1, R10.2, R18.1, SW1.1, U1.13 (~SDN), U1.15 (FR), U1.17 (+VS), U2.1 (VBAT), U2.19 (VDD), U2.32 (VDD), U2.48 (VDD), U2.64 (VDD), U3.6 (VDD)
+3.3VA: C16.1, C17.1, FB1.1, U2.13 (VDDA)
+5V: C21.1, C22.1, J4.1 (VBUS), U3.7 (VREGIN), U3.8 (VBUS)
/AD8232_LOD_N: U1.12 (LO+), U2.10 (PC2)
/AD8232_LOD_P: U1.11 (LO-), U2.9 (PC1)
/ADC1_IN1: C1.2, J2.1, R9.2, U1.10 (OUT), U2.14 (PA0)
/BOOT0: R12.2, U2.60 (BOOT0)
/HPDRIVE: C6.1, U1.1 (HPDRIVE)
/HPSENSE: C6.2, R14.1, U1.20 (HPSENSE)
/HR_LED_K: D1.1 (K), R16.1
/IAOUT: R2.2, R13.2, U1.19 (IAOUT)
/IN+: R5.1, U1.2 (+IN)
/IN-: R6.1, U1.3 (-IN)
/LA: J1.2, R1.2, R5.2
/LED: D1.2 (A), U2.21 (PA5)
/NRST: C8.1, U2.7 (NRST)
/OPAMP+: C3.1, R4.1, U1.7 (OPAMP+)
/OPAMP-: R8.2, R9.1, U1.9 (OPAMP-)
/PWR_LED_K: D2.1 (K), R17.1
/RA: J1.4, R3.2, R6.2
/RCC_OSC_IN: C2.1, U2.5 (PF0), Y1.1
/RCC_OSC_OUT: C5.1, U2.6 (PF1), Y1.3
/REFIN: C12.2, R10.1, R11.1, U1.18 (REFIN)
/REFOUT: C3.2, C15.1, R8.1, U1.8 (REFOUT)
/RL: J1.3, R7.2
/RLD: C4.2, R7.1, U1.5 (RLD)
/RLDFB: C4.1, U1.4 (RLDFB)
/SW: C15.2, R15.2, U1.6 (SW)
/SW_BOOT0: R12.1, SW1.2
/TCK: J3.3, U2.49 (PA14)
/TMS: J3.2, U2.46 (PA13)
/USART2_TX: U2.16 (PA2), U3.17 (RXD)
/USB_D+: J4.3 (D+), U3.4 (D+)
/USB_D-: J4.2 (D-), U3.5 (D-)
GND: C2.2, C5.2, C7.2, C8.2, C9.2, C10.2, C11.2, C12.1, C13.2, C14.2, C16.2, C17.2, C18.2, C19.2, C20.2, C21.2, C22.2, J2.2, J3.4, J4.5 (GND), R11.2, R16.2, R17.2, SW1.3, U1.14 (AC/~DC), U1.16 (GND), U1.PAD (GND_PAD), U2.12 (VSSA), U2.18 (VSS), U2.31 (VSS), U2.47 (VSS), U2.63 (VSS), U3.3 (GND), U3.12 (GND), U3.21 (GND), Y1.2, Y1.4
unnamed: C1.1, R2.1, R4.2
unnamed: R13.1, R14.2, R15.1
unnamed: R18.2, U3.9 (~RST)

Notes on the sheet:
Mounting Holes
Bypass capacitor values taken directly from IC datasheet
CL = 2*(CL0-Cs) = 2*(10-5) pF = 10 pF
1 x 100 nF per VDD pin
Microcontroller
Pin-out using STM32CubeIDE
ECG front-end
Power supply
USB-UART interface
Oscillator
ec-stingy
See SPICE model & README for component value & circuitry details

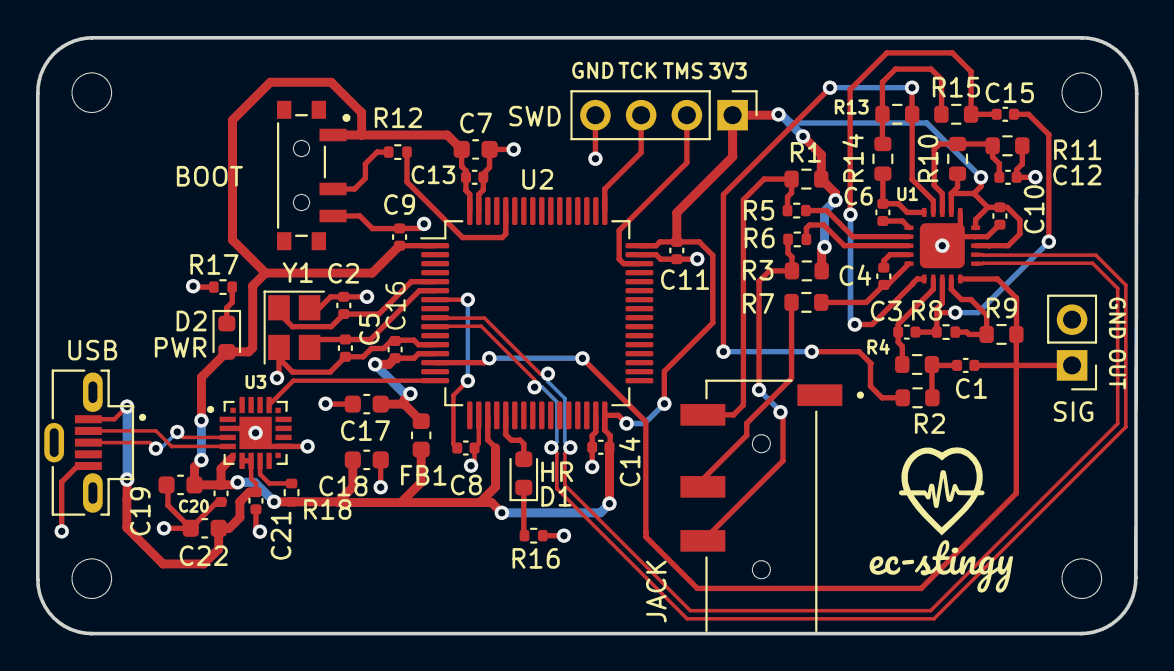
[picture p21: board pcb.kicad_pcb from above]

Board: 2 copper layers, 61.0 x 33.1 mm, 56 parts (0 on the bottom side), 38 nets.

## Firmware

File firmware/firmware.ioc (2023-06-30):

#MicroXplorer Configuration settings - do not modify
ADC1.Channel-2\#ChannelRegularConversion=ADC_CHANNEL_1
ADC1.ContinuousConvMode=ENABLE
ADC1.DMAContinuousRequests=ENABLE
ADC1.IPParameters=Rank-2\#ChannelRegularConversion,master,Channel-2\#ChannelRegularConversion,SamplingTime-2\#ChannelRegularConversion,SamplingTimeOPAMP-2\#ChannelRegularConversion,OffsetNumber-2\#ChannelRegularConversion,Offset-2\#ChannelRegularConversion,NbrOfConversionFlag,ContinuousConvMode,DMAContinuousRequests,SubFamily
ADC1.NbrOfConversionFlag=1
ADC1.Offset-2\#ChannelRegularConversion=0
ADC1.OffsetNumber-2\#ChannelRegularConversion=ADC_OFFSET_NONE
ADC1.Rank-2\#ChannelRegularConversion=1
ADC1.SamplingTime-2\#ChannelRegularConversion=ADC_SAMPLETIME_1CYCLE_5
ADC1.SamplingTimeOPAMP-2\#ChannelRegularConversion=ADC_SAMPLETIME_61CYCLES_5
ADC1.SubFamily=STM32F334x8
ADC1.master=1
CAD.formats=
CAD.pinconfig=
CAD.provider=
Dma.ADC1.1.Direction=DMA_PERIPH_TO_MEMORY
Dma.ADC1.1.Instance=DMA1_Channel1
Dma.ADC1.1.MemDataAlignment=DMA_MDATAALIGN_HALFWORD
Dma.ADC1.1.MemInc=DMA_MINC_ENABLE
Dma.ADC1.1.Mode=DMA_CIRCULAR
Dma.ADC1.1.PeriphDataAlignment=DMA_PDATAALIGN_HALFWORD
Dma.ADC1.1.PeriphInc=DMA_PINC_DISABLE
Dma.ADC1.1.Priority=DMA_PRIORITY_LOW
Dma.ADC1.1.RequestParameters=Instance,Direction,PeriphInc,MemInc,PeriphDataAlignment,MemDataAlignment,Mode,Priority
Dma.Request0=USART2_TX
Dma.Request1=ADC1
Dma.RequestsNb=2
Dma.USART2_TX.0.Direction=DMA_MEMORY_TO_PERIPH
Dma.USART2_TX.0.Instance=DMA1_Channel7
Dma.USART2_TX.0.MemDataAlignment=DMA_MDATAALIGN_BYTE
Dma.USART2_TX.0.MemInc=DMA_MINC_ENABLE
Dma.USART2_TX.0.Mode=DMA_NORMAL
Dma.USART2_TX.0.PeriphDataAlignment=DMA_PDATAALIGN_BYTE
Dma.USART2_TX.0.PeriphInc=DMA_PINC_DISABLE
Dma.USART2_TX.0.Priority=DMA_PRIORITY_LOW
Dma.USART2_TX.0.RequestParameters=Instance,Direction,PeriphInc,MemInc,PeriphDataAlignment,MemDataAlignment,Mode,Priority
File.Version=6
GPIO.groupedBy=Group By Peripherals
KeepUserPlacement=false
Mcu.CPN=STM32F334R8T6
Mcu.Family=STM32F3
Mcu.IP0=ADC1
Mcu.IP1=DMA
Mcu.IP2=NVIC
Mcu.IP3=RCC
Mcu.IP4=SYS
Mcu.IP5=TIM6
Mcu.IP6=USART2
Mcu.IPNb=7
Mcu.Name=STM32F334R(6-8)Tx
Mcu.Package=LQFP64
Mcu.Pin0=PC14 / OSC32_IN
Mcu.Pin1=PC15 / OSC32_OUT
Mcu.Pin10=PA13
Mcu.Pin11=PA14
Mcu.Pin12=PB3
Mcu.Pin13=VP_TIM6_VS_ClockSourceINT
Mcu.Pin2=PF0 / OSC_IN
Mcu.Pin3=PF1 / OSC_OUT
Mcu.Pin4=PC0
Mcu.Pin5=PC1
Mcu.Pin6=PA0
Mcu.Pin7=PA2
Mcu.Pin8=PA3
Mcu.Pin9=PA5
Mcu.PinsNb=14
Mcu.ThirdPartyNb=0
Mcu.UserConstants=
Mcu.UserName=STM32F334R8Tx
MxCube.Version=6.8.1
MxDb.Version=DB.6.0.81
NVIC.BusFault_IRQn=true\:0\:0\:false\:false\:true\:false\:false\:false
NVIC.DMA1_Channel1_IRQn=true\:0\:0\:false\:false\:true\:false\:true\:true
NVIC.DMA1_Channel7_IRQn=true\:0\:0\:false\:false\:true\:false\:true\:true
NVIC.DebugMonitor_IRQn=true\:0\:0\:false\:false\:true\:false\:false\:false
NVIC.ForceEnableDMAVector=true
NVIC.HardFault_IRQn=true\:0\:0\:false\:false\:true\:false\:false\:false
NVIC.MemoryManagement_IRQn=true\:0\:0\:false\:false\:true\:false\:false\:false
NVIC.NonMaskableInt_IRQn=true\:0\:0\:false\:false\:true\:false\:false\:false
NVIC.PendSV_IRQn=true\:0\:0\:false\:false\:true\:false\:false\:false
NVIC.PriorityGroup=NVIC_PRIORITYGROUP_0
NVIC.SVCall_IRQn=true\:0\:0\:false\:false\:true\:false\:false\:false
NVIC.SysTick_IRQn=true\:0\:0\:false\:false\:true\:true\:true\:false
NVIC.TIM6_DAC1_IRQn=true\:0\:0\:false\:false\:true\:true\:true\:true
NVIC.UsageFault_IRQn=true\:0\:0\:false\:false\:true\:false\:false\:false
PA0.Mode=IN1-Single-Ended
PA0.Signal=ADC1_IN1
PA13.GPIOParameters=GPIO_Label
PA13.GPIO_Label=TMS
PA13.Locked=true
PA13.Mode=Serial_Wire
PA13.Signal=SYS_JTMS-SWDIO
PA14.GPIOParameters=GPIO_Label
PA14.GPIO_Label=TCK
PA14.Locked=true
PA14.Mode=Serial_Wire
PA14.Signal=SYS_JTCK-SWCLK
PA2.Mode=Asynchronous
PA2.Signal=USART2_TX
PA3.Mode=Asynchronous
PA3.Signal=USART2_RX
PA5.GPIOParameters=GPIO_Label
PA5.GPIO_Label=LED
PA5.Locked=true
PA5.Signal=GPIO_Output
PB3.GPIOParameters=GPIO_Label
PB3.GPIO_Label=SWO
PB3.Locked=true
PB3.Signal=SYS_JTDO-TRACESWO
PC0.GPIOParameters=GPIO_Label
PC0.GPIO_Label=AD8232_LOD_P
PC0.Locked=true
PC0.Signal=GPIO_Input
PC1.GPIOParameters=GPIO_Label
PC1.GPIO_Label=AD8232_LOD_N
PC1.Locked=true
PC1.Signal=GPIO_Input
PC14\ /\ OSC32_IN.Locked=true
PC14\ /\ OSC32_IN.Signal=RCC_OSC32_IN
PC15\ /\ OSC32_OUT.GPIOParameters=GPIO_Label
PC15\ /\ OSC32_OUT.GPIO_Label=RCC_OSC32_OUT
PC15\ /\ OSC32_OUT.Locked=true
PC15\ /\ OSC32_OUT.Signal=RCC_OSC32_OUT
PF0\ /\ OSC_IN.Locked=true
PF0\ /\ OSC_IN.Mode=HSE-External-Oscillator
PF0\ /\ OSC_IN.Signal=RCC_OSC_IN
PF1\ /\ OSC_OUT.Locked=true
PF1\ /\ OSC_OUT.Mode=HSE-External-Oscillator
PF1\ /\ OSC_OUT.Signal=RCC_OSC_OUT
PinOutPanel.RotationAngle=0
ProjectManager.AskForMigrate=true
ProjectManager.BackupPrevious=false
ProjectManager.CompilerOptimize=6
ProjectManager.ComputerToolchain=false
ProjectManager.CoupleFile=false
ProjectManager.CustomerFirmwarePackage=
ProjectManager.DefaultFWLocation=true
ProjectManager.DeletePrevious=true
ProjectManager.DeviceId=STM32F334R8Tx
ProjectManager.FirmwarePackage=STM32Cube FW_F3 V1.11.4
ProjectManager.FreePins=false
ProjectManager.HalAssertFull=false
ProjectManager.HeapSize=0x200
ProjectManager.KeepUserCode=true
ProjectManager.LastFirmware=true
ProjectManager.LibraryCopy=1
ProjectManager.MainLocation=Core/Src
ProjectManager.NoMain=false
ProjectManager.PreviousToolchain=
ProjectManager.ProjectBuild=false
ProjectManager.ProjectFileName=firmware.ioc
ProjectManager.ProjectName=firmware
ProjectManager.ProjectStructure=
ProjectManager.RegisterCallBack=
ProjectManager.StackSize=0x400
ProjectManager.TargetToolchain=STM32CubeIDE
ProjectManager.ToolChainLocation=
ProjectManager.UnderRoot=true
ProjectManager.functionlistsort=1-SystemClock_Config-RCC-false-HAL-false,2-MX_GPIO_Init-GPIO-false-HAL-true,3-MX_DMA_Init-DMA-false-HAL-true,4-MX_USART2_UART_Init-USART2-false-HAL-true,5-MX_ADC1_Init-ADC1-false-HAL-true,6-MX_TIM6_Init-TIM6-false-HAL-true
RCC.ADC12outputFreq_Value=64000000
RCC.AHBFreq_Value=64000000
RCC.APB1CLKDivider=RCC_HCLK_DIV2
RCC.APB1Freq_Value=32000000
RCC.APB1TimFreq_Value=64000000
RCC.APB2Freq_Value=64000000
RCC.APB2TimFreq_Value=64000000
RCC.CortexFreq_Value=64000000
RCC.FCLKCortexFreq_Value=64000000
RCC.FLatency-AdvancedSettings=FLASH_LATENCY_2
RCC.FamilyName=M
RCC.HCLKFreq_Value=64000000
RCC.HRTIM1Freq_Value=64000000
RCC.HSEPLLFreq_Value=8000000
RCC.HSE_VALUE=8000000
RCC.HSIPLLFreq_Value=4000000
RCC.HSI_VALUE=8000000
RCC.I2C1Freq_Value=8000000
RCC.IPParameters=ADC12outputFreq_Value,AHBFreq_Value,APB1CLKDivider,APB1Freq_Value,APB1TimFreq_Value,APB2Freq_Value,APB2TimFreq_Value,CortexFreq_Value,FCLKCortexFreq_Value,FLatency-AdvancedSettings,FamilyName,HCLKFreq_Value,HRTIM1Freq_Value,HSEPLLFreq_Value,HSE_VALUE,HSIPLLFreq_Value,HSI_VALUE,I2C1Freq_Value,LSE_VALUE,LSI_VALUE,MCOFreq_Value,PLLCLKFreq_Value,PLLMCOFreq_Value,PLLMUL,RTCFreq_Value,RTCHSEDivFreq_Value,SYSCLKFreq_VALUE,SYSCLKSourceVirtual,TIM1Freq_Value,TIM2Freq_Value,USART1Freq_Value,VCOOutput2Freq_Value
RCC.LSE_VALUE=32768
RCC.LSI_VALUE=40000
RCC.MCOFreq_Value=64000000
RCC.PLLCLKFreq_Value=64000000
RCC.PLLMCOFreq_Value=64000000
RCC.PLLMUL=RCC_PLL_MUL16
RCC.RTCFreq_Value=40000
RCC.RTCHSEDivFreq_Value=250000
RCC.SYSCLKFreq_VALUE=64000000
RCC.SYSCLKSourceVirtual=RCC_SYSCLKSOURCE_PLLCLK
RCC.TIM1Freq_Value=64000000
RCC.TIM2Freq_Value=64000000
RCC.USART1Freq_Value=32000000
RCC.VCOOutput2Freq_Value=4000000
TIM6.IPParameters=Prescaler,Period
TIM6.Period=422
TIM6.Prescaler=421
USART2.BaudRate=115200
USART2.IPParameters=VirtualMode-Asynchronous,BaudRate
USART2.VirtualMode-Asynchronous=VM_ASYNC
VP_TIM6_VS_ClockSourceINT.Mode=Enable_Timer
VP_TIM6_VS_ClockSourceINT.Signal=TIM6_VS_ClockSourceINT
board=NUCLEO-F334R8
boardIOC=true
isbadioc=false

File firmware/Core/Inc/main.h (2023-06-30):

/* USER CODE BEGIN Header */
/**
  ******************************************************************************
  * @file           : main.h
  * @brief          : Header for main.c file.
  *                   This file contains the common defines of the application.
  ******************************************************************************
  * @attention
  *
  * Copyright (c) 2023 STMicroelectronics.
  * All rights reserved.
  *
  * This software is licensed under terms that can be found in the LICENSE file
  * in the root directory of this software component.
  * If no LICENSE file comes with this software, it is provided AS-IS.
  *
  ******************************************************************************
  */
/* USER CODE END Header */

/* Define to prevent recursive inclusion -------------------------------------*/
#ifndef __MAIN_H
#define __MAIN_H

#ifdef __cplusplus
extern "C" {
#endif

/* Includes ------------------------------------------------------------------*/
#include "stm32f3xx_hal.h"

/* Private includes ----------------------------------------------------------*/
/* USER CODE BEGIN Includes */

/* USER CODE END Includes */

/* Exported types ------------------------------------------------------------*/
/* USER CODE BEGIN ET */

/* USER CODE END ET */

/* Exported constants --------------------------------------------------------*/
/* USER CODE BEGIN EC */

/* USER CODE END EC */

/* Exported macro ------------------------------------------------------------*/
/* USER CODE BEGIN EM */

/* USER CODE END EM */

/* Exported functions prototypes ---------------------------------------------*/
void Error_Handler(void);

/* USER CODE BEGIN EFP */

/* USER CODE END EFP */

/* Private defines -----------------------------------------------------------*/
#define RCC_OSC32_OUT_Pin GPIO_PIN_15
#define RCC_OSC32_OUT_GPIO_Port GPIOC
#define AD8232_LOD_P_Pin GPIO_PIN_0
#define AD8232_LOD_P_GPIO_Port GPIOC
#define AD8232_LOD_N_Pin GPIO_PIN_1
#define AD8232_LOD_N_GPIO_Port GPIOC
#define LED_Pin GPIO_PIN_5
#define LED_GPIO_Port GPIOA
#define TMS_Pin GPIO_PIN_13
#define TMS_GPIO_Port GPIOA
#define TCK_Pin GPIO_PIN_14
#define TCK_GPIO_Port GPIOA
#define SWO_Pin GPIO_PIN_3
#define SWO_GPIO_Port GPIOB

/* USER CODE BEGIN Private defines */

/* USER CODE END Private defines */

#ifdef __cplusplus
}
#endif

#endif /* __MAIN_H */

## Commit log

2022-07-07 working circuit
2022-10-11 i goofed something with the circuit lol
2022-12-23 finished ad8232 breakout pcb
    [AD8232.step, AD8232_breakout-B_Cu.gbr, AD8232_breakout-B_Mask.gbr, AD8232_breakout-B_Paste.gbr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]
2023-01-09 added another application circuit spice file
2023-01-09 added missing capcaitor and fixed voltage sources
2023-02-16 added script to print serial port data to file
2023-04-13 peak detection working but sample rate caps at ~140 Hz
2023-04-14 added C program to test signal processing
    [scope.csv]
2023-05-09 first filter works in C
    [output.csv]
2023-05-09 waveforms look good
    [output.csv]
2023-05-12 peak detection implemented but not working
    [output.csv]
2023-05-12 last commit before filter restructuring
    [output.csv]
2023-05-17 added macros
    [output.csv]
2023-05-18 peak detection implemented but weird linter warning
    [output.csv, scope_reversed.csv]
2023-05-18 mostly accurate readings
    [scope.csv, scope_reversed.csv]
2023-05-18 readings mostly accurate
    [output.csv, scope_clean.csv]
2023-05-19 peak detection finds max in original signal. works in MATLAB, one beat wrong in C
    [output.csv, scope_clean.csv]
2023-05-28 current state
2023-05-29 stack reallocation works but need to re-work C prototype program to use smaller buffers wherever possible
2023-05-30 highpass filter works
2023-06-01 algo signals looking good
    [output.csv, scope.csv]
2023-06-02 non-blocking works!
    [AD8232_breakout-B_Cu.gbr, AD8232_breakout-B_Mask.gbr, AD8232_breakout-B_Paste.gbr, AD8232_breakout-B_Silkscreen.gbr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]
2023-06-05 prints rounded val to uart
2023-06-09 working state
    [output.csv, scope2.csv]
2023-06-14 gui good, notch filter working in C program but code could be made cleaner
    [output.csv]
2023-06-14 cleaned up Octave scripts
    [output.csv]
2023-06-15 put notch filter before low pass
    [output.csv]
2023-06-15 added notch filtering before low pass on STM32 but offset is weird
    [output.csv, scope2.csv]
2023-06-15 fixed minor things after merging experiment into main
    [output.csv]
2023-06-16 added more comments and updated .gitignore
    [scope2.csv]
2023-06-16 remove cached files
    [output.csv]
2023-06-16 added comments to stm32 main()
2023-06-27 fixed grounding on spice model, progress on schematic
    [AD8232.step, ec-stingy.kicad_pcb, ec-stingy.kicad_sch]
2023-06-29 reconstructed schematic
    [ec-stingy.kicad_sch]
2023-06-30 assigning footprints progress
    [ec-stingy.kicad_sch]
2023-07-05 progress on layout
    [105133-0011.step, CP2102N-A02-GQFN20R.step, PCM12SMTR.step, PJ-320D-A.step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]
2023-07-07 more pcb progress
    [ec-stingy.kicad_pcb, ec-stingy.kicad_sch]
2023-07-08 high pass filter visual
2023-07-08 triangle filter added
2023-07-08 restored Octave algo script
    [ec-stingy.kicad_pcb, ec-stingy.kicad_sch]
2023-07-19 minor readme changes
    [pcb.kicad_pcb, pcb.kicad_sch]
2023-07-19 pcb finished
    [bom.csv, component_placement.csv, pcb-B_Cu.gbr, pcb-B_Mask.gbr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]
2023-07-20 readme prog
    [pcb.kicad_pcb]
2023-08-08 more readme updates
    [bom_with_prices.csv]
